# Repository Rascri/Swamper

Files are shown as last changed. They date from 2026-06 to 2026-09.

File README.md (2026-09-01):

# Swaby

## Descripción

**Swaby** es un proyecto investigativo orientado al desarrollo de un sistema portátil de monitoreo biomédico. El prototipo permite adquirir y visualizar en tiempo real información relacionada con la actividad cardíaca y el movimiento del usuario.

El sistema utiliza un **ESP32** como unidad principal de procesamiento, conectado a un sensor **AD8232** para la adquisición del electrocardiograma (ECG), un **DS18B20** para la medición de temperatura y un **MPU-6050** para el análisis de movimiento y postura.

Los datos obtenidos son procesados por el ESP32 y enviados mediante **Bluetooth** a una PC para su visualización y registro.

## Enfoque investigativo

El desarrollo de Swaby se planteó como un proyecto investigativo, además de la construcción de un prototipo funcional. Durante las pruebas se analizaron las condiciones necesarias para obtener una señal de ECG estable y las limitaciones del sistema.

Se comprobó que el ECG funciona correctamente cuando el usuario se encuentra en reposo, pero presenta importantes perturbaciones durante el movimiento. El principal problema identificado fue el ruido generado por la actividad y el movimiento muscular, que se superpone a la señal cardíaca y genera artefactos que dificultan su correcta interpretación.

A pesar del filtrado incorporado en el AD8232, filtrado por software y los recursos disponibles para el proyecto no fue posible eliminar estas interferencias de manera suficiente como para obtener una señal de ECG confiable durante el movimiento. Por este motivo, el monitoreo cardíaco se consideró funcional bajo condiciones de reposo, pero limitado durante la actividad física.

También se detectaron interferencias externas durante las primeras pruebas, relacionadas con la alimentación y la calidad de los electrodos. Estas fueron reducidas mediante el aislamiento de la fuente de alimentación utilizada en el laboratorio y el reemplazo de los electrodos por otros de mayor calidad.

## Software

El **ESP32** se encarga de adquirir los datos de los sensores y transmitirlos mediante Bluetooth.

Para la visualización y registro de los datos se desarrolló una aplicación en **Processing**, encargada de recibir la información enviada por el ESP32 y representarla de forma gráfica en tiempo real.

La aplicación permite visualizar principalmente:

* Señal de ECG y BPM en tiempo real.
* Datos de temperatura.
* Información proveniente del MPU-6050.

La comunicación entre el prototipo y la aplicación se realiza de forma inalámbrica mediante **Bluetooth**, permitiendo separar físicamente el sistema de adquisición de la interfaz de visualización.

## Estado del proyecto

El prototipo logró cumplir con el objetivo planteado, permitiendo la adquisición y visualización en tiempo real de las variables estudiadas.

El repositorio contiene el código, componentes, diagramas y documentación correspondiente al desarrollo de **Swaby**.

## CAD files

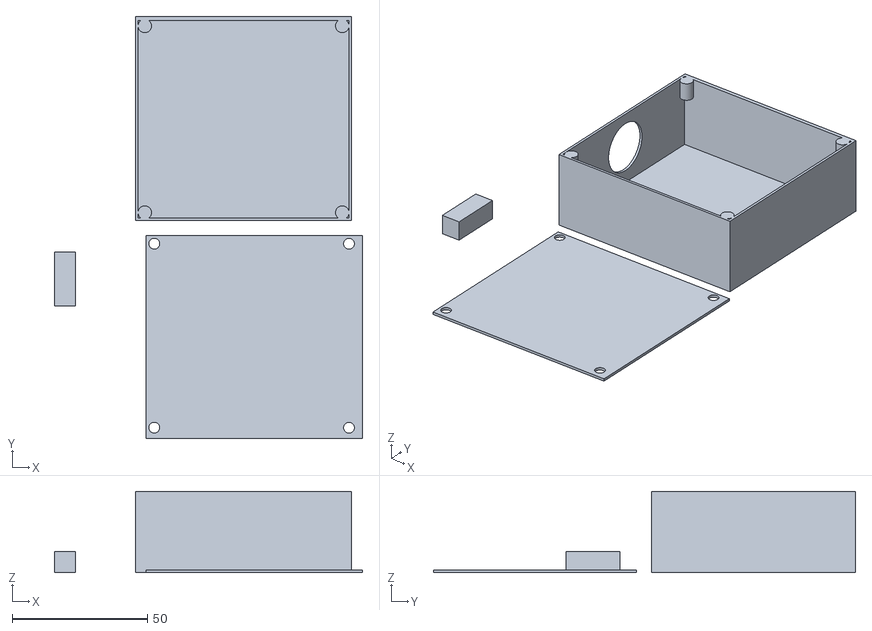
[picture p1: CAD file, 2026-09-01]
Diseño 3D/Caja.stl
113.9 x 156.0 x 30.0

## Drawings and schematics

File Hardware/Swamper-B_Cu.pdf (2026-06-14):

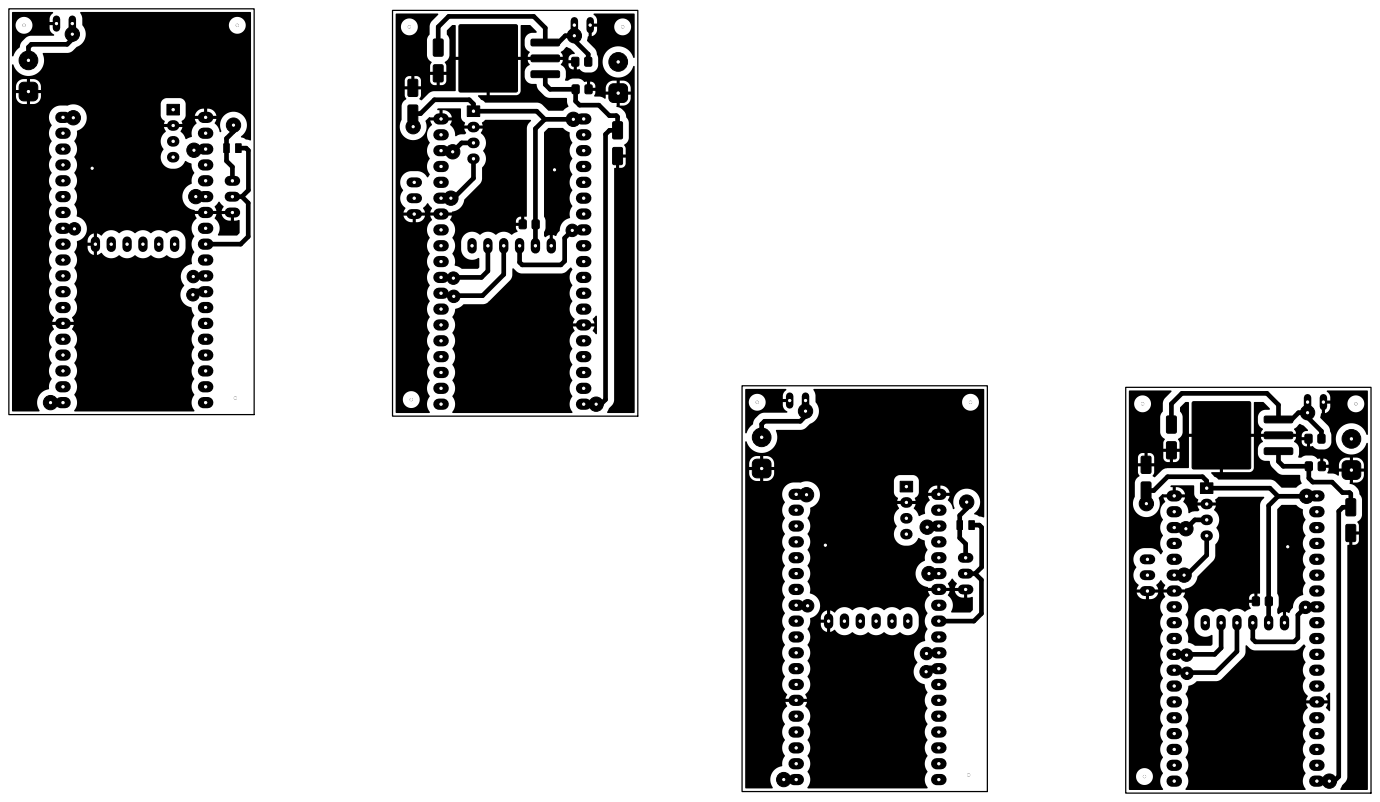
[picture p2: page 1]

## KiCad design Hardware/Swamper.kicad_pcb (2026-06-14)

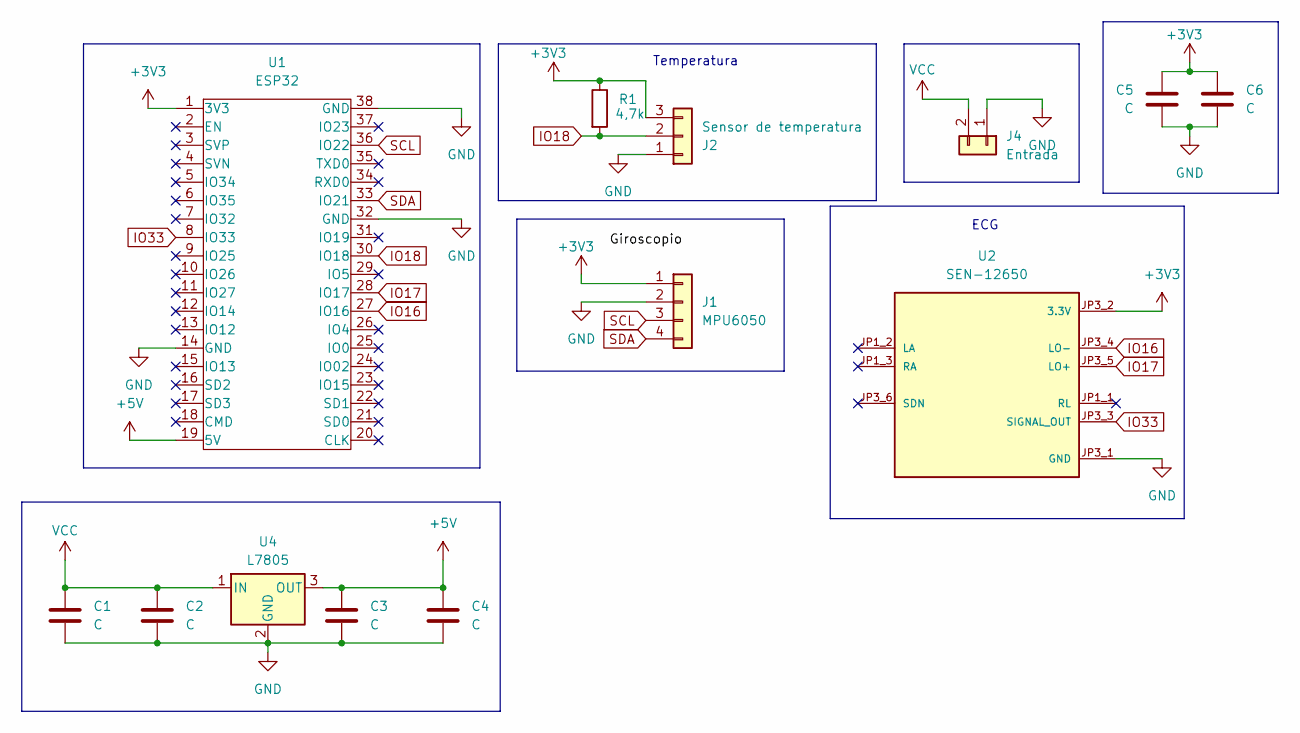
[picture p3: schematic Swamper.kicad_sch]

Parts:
C1, C4, C6: C; C_Elec_5x5.8
C2, C3, C5: C; C_0805_2012Metric_Pad1.18x1.45mm_HandSolder
J1: MPU6050; MPU6050_Module
J2: Sensor de temperatura; JST-3V
J4: Entrada; AMASS_XT30UPB-F_1x02_P5.0mm_Vertical
R1: 4,7k; R_0805
U1: ESP32; ESP32S
U2: SEN-12650; MODULE_SEN-12650; PARTREV V10
U4: L7805; TO-263-3_TabPin2

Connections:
+3V3: C5.1, C6.1, J1.1, J2.3, R1.1, U1.1 (3V3), U2.JP3_2 (3.3V)
+5V: C3.1, C4.1, U1.19 (5V), U4.3 (OUT)
GND: C1.2, C2.2, C3.2, C4.2, C5.2, C6.2, J1.2, J2.1, J4.1, U1.14 (GND), U1.32 (GND), U1.38 (GND), U2.JP3_1 (GND), U4.2 (GND); also elsewhere on the board
IO16: U1.27 (IO16), U2.JP3_4 (LO-)
IO17: U1.28 (IO17), U2.JP3_5 (LO+)
IO18: J2.2, R1.2, U1.30 (IO18)
IO33: U1.8 (IO33), U2.JP3_3 (SIGNAL_OUT)
SCL: J1.3, U1.36 (IO22)
SDA: J1.4, U1.33 (IO21)
VCC: C1.1, C2.1, J4.2, U4.1 (IN); also elsewhere on the board

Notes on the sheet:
ECG
Temperatura

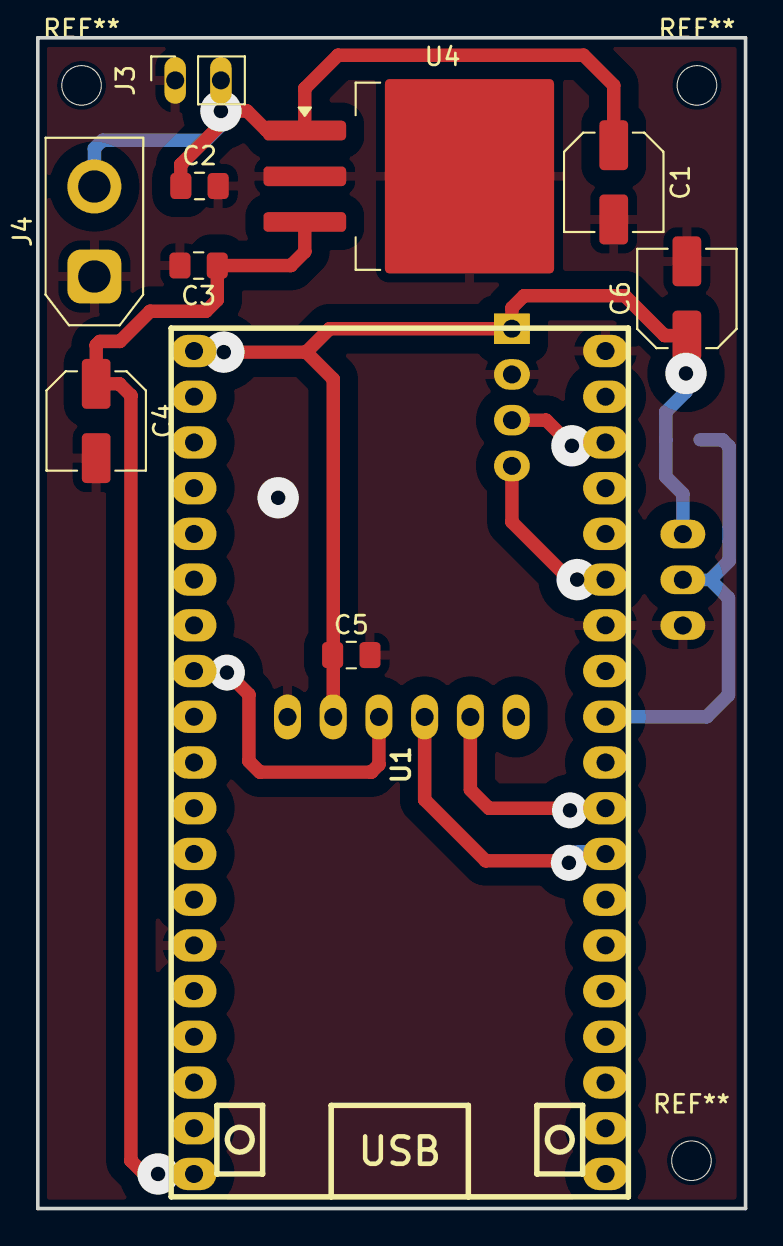
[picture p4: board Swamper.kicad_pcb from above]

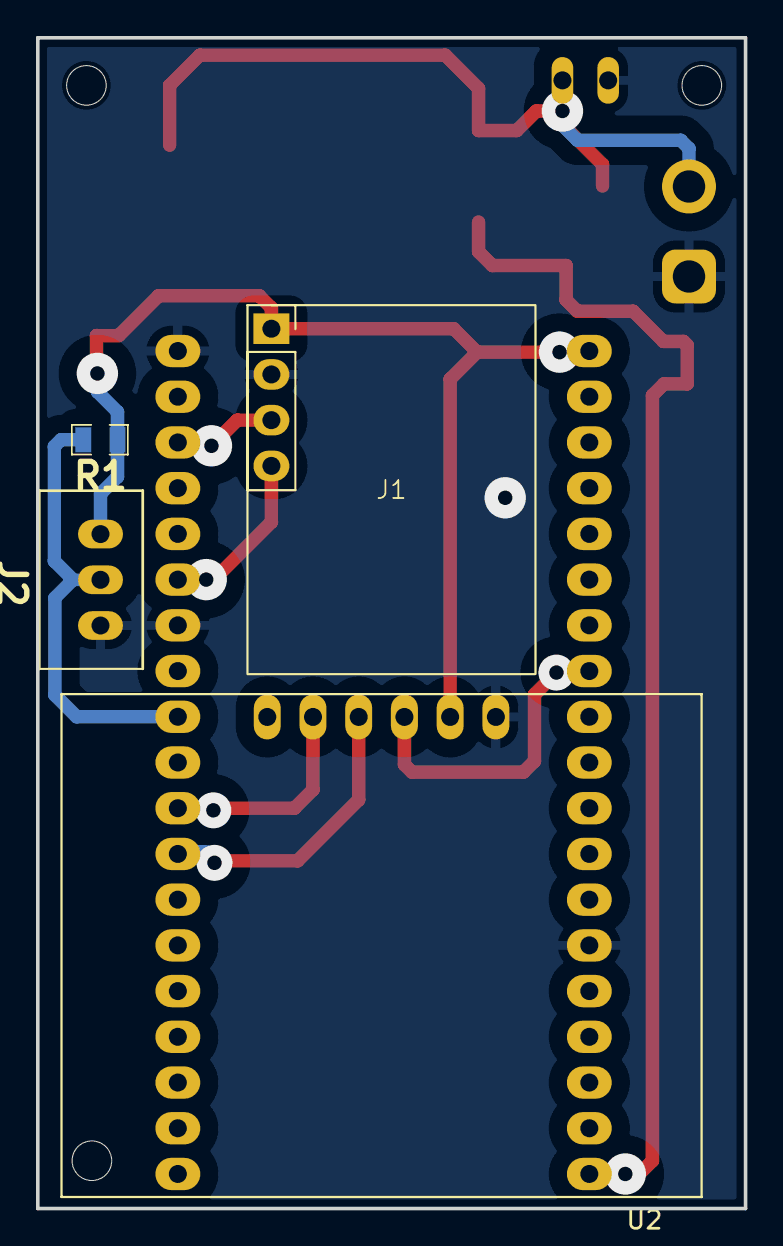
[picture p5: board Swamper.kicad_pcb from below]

Board: 2 copper layers, 39.3 x 65.0 mm, 14 parts (4 on the bottom side), 10 nets.

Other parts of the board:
J3: Entrada; PinSocket_1x02_P2.54mm_Vertical

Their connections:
GND: J3.1; also elsewhere on the board
VCC: J3.2; also elsewhere on the board
